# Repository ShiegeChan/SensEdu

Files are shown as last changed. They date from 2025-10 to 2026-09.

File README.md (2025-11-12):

<p align="center">
  
</p>

<p align="center"><b>Ultrasonic Ranging & Detection Development Shield for Arduino GIGA R1</b><br>
Designed for education - easy entry into ultrasonic sensing and research</p>

<p align="center">
  <a href="https://github.com/ShiegeChan/SensEdu/releases/" target="_blank">
    
  </a>
  <a href="https://github.com/ShiegeChan/SensEdu/commits/main" target="_blank">
    
  </a>
</p>

<b>
<p align="center">
	<a href="https://github.com/ShiegeChan/SensEdu/releases" target="_blank">Download</a> ·
	<a href="https://sensedu-shield.com/getting-started/" target="_blank">Getting Started</a> ·
	<a href="https://sensedu-shield.com/projects/" target="_blank">Example Projects</a> ·
	<a href="https://sensedu-shield.com" target="_blank">Documentation</a> ·
	<a href="https://sensedu-shield.com/contributing/" target="_blank">Contribution</a>
</p>
</b>

## Features

* **Custom Shield Design** for <a href="https://docs.arduino.cc/hardware/giga-r1-wifi/?queryID=undefined" target="_blank">Arduino GIGA R1 WiFi</a> and mechanically compatible boards (e.g., <a href="https://www.infineon.com/evaluation-board/KIT-A2G-TC375-ARD-SB" target="_blank">AURIX™ TC375 Shieldbuddy</a>). It extends the board with sensors:
  * **4x Infineon MEMS microphones**: capable of operating in ultrasonic range at approx. 20-80 kHz (<a href="https://www.infineon.com/assets/row/public/documents/24/49/infineon-im73a135-datasheet-en.pdf" target="_blank">datasheet</a>).
  * **2x Ultrasonic Transducers**: transmit ultrasonic waves with a center frequency of ~33kHz (<a href="https://www.farnell.com/datasheets/4413630.pdf?_gl=1*1fltz5c*_gcl_au*MTQwMTY3ODgxOC4xNzI2NDc2MDYw" target="_blank">datasheet</a>).
  * **2x Instrumentation Amplifiers**: providing 4x channels total, routed to external pin headers for connecting additional sensors such as surface EMG electrodes (<a href="https://www.analog.com/media/en/technical-documentation/data-sheets/ad8222.pdf" target= "_blank">datasheet</a>).
  * **1x Infineon Barometric Air Pressure Sensor**: provides pressure and temperature measurements; ideal for indoor and outdoor navigation, weather stations, drones, and more (<a href="https://www.infineon.com/dgdl/Infineon-DPS310-DataSheet-v01_02-EN.pdf?fileId=5546d462576f34750157750826c42242" target="_blank">datasheet</a>).
* **Low-Level SensEdu Library** for Arduino GIGA R1 that serves as a basic abstraction layer for the STM32H747 peripherals and provides default configurations for all sensors. It is implemented at the register level based on <a href="https://www.st.com/resource/en/reference_manual/rm0399-stm32h745755-and-stm32h747757-advanced-armbased-32bit-mcus-stmicroelectronics.pdf" target="_blank">STM32H747 Reference Manual</a> and <a href="https://developer.arm.com/documentation/ddi0403/latest/" target="_blank"> Armv7-M Architecture Reference Manual</a>, ensuring simplicity and expandability. Extensive examples are included to demonstrate library's functionality.
* **Example projects** show how to use SensEdu to achieve your learning goals. See the full implementation for pulsed time-of-flight distance measurements, FMCW ranging, FSK-modulated communication, a weather station, and other projects.
* **MATLAB scripts** enable visualization and post-processing of recorded data transferred via USB or Wi-Fi.

## Preview

<p align="center" style="margin:0">
  
  
  
  
  
</p>

## Installation

1. Download the latest release version from the <a href="https://github.com/ShiegeChan/SensEdu/releases" target="_blank">Download page</a>.
2. Extract the downloaded files and place the **libraries** folder into: `C:\Users\your_username\Documents\Arduino\`.
3. The **projects** folder can be placed anywhere in your system.
4. Open the <a href="https://www.arduino.cc/en/software" target="_blank">Arduino IDE</a> and install **Arduino Giga R1 board package** via the Boards Manager.

<p align="left" style="margin:0">
  
</p>
<p align="left" style="margin:0">
  
</p>

## Starting a Project

To get started, you can explore the hardware interface by following the examples provided in the SensEdu library (`Arduino\libraries\SensEdu\examples\`). A detailed description of all functions can be found in the <a href="https://sensedu-shield.com/library/" target="_blank">Documentation</a> under the "SensEdu Library" section.

In the `projects/` directory, you will find several complete projects designed for this board, including:
* **Ultrasonic Pulse-Echo Ranging**
* **Ultrasonic Pulse-Echo Ranging with Wi-Fi + GUI** - *in progress (25%)*
* **Ultrasonic Chirp Generation**
* **Ultrasonic FMCW Ranging**
* **Ultrasonic Doppler Velocimeter** - *coming soon*
* **Ultrasonic FSK Communication Link** - *coming soon*
* **EMG BioInputs** - *in progress (75%)*
* **Weather Station** - *in progress (50%)*

Detailed overview for each project is available in the "Projects" section of the <a href="https://sensedu-shield.com/projects/" target="_blank">Documentation</a>.

## Support

If you would like to contribute, please open a pull request!
Suggest improvements or check out already opened <a href="https://github.com/ShiegeChan/SensEdu/issues" target="_blank">issues</a> to help fix bugs or add new features.

## Acknowledgments

SensEdu was made possible thanks to these freely available tools:

* [Arduino] and [Arduino IDE 2.x]
* [XENSIV™ Digital Pressure Sensor Arduino Library]
* [STM32H747 Documentation] and [STM32CubeMX]
* [Jekyll] and [Just the Docs] template
* [KiCAD]

## License

* [**GPL-3.0 license**](https://github.com/ShiegeChan/SensEdu/blob/main/LICENSE)

[Arduino IDE 2.x]: https://github.com/arduino/arduino-ide
[Arduino]: https://www.arduino.cc/
[XENSIV™ Digital Pressure Sensor Arduino Library]: https://github.com/Infineon/arduino-xensiv-dps3xx
[STM32H747 Documentation]: https://www.st.com/en/microcontrollers-microprocessors/stm32h747-757/documentation.html
[STM32CubeMX]: https://www.st.com/en/development-tools/stm32cubemx.html
[Jekyll]: https://jekyllrb.com/
[Just the Docs]: https://github.com/just-the-docs/just-the-docs/tree/main
[STM32H747]: https://www.st.com/en/microcontrollers-microprocessors/stm32h747-757.html
[Arduino GIGA R1 WiFi]: https://docs.arduino.cc/hardware/giga-r1-wifi/
[KiCad]: https://www.kicad.org/

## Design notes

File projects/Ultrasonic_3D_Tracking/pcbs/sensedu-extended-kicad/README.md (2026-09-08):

# Extended SensEdu Shield (8 Microphones)

> [!WARNING]
> This PCB is a messy prototype that has never been cleaned up, and it may not work at all.
> It was created for the sole purpose of quickly testing an 8-microphone setup on a very old
> SensEdu revision, and is published for reference rather than for reproduction.

If you need an 8-microphone version, please contact us and we will help you with it.

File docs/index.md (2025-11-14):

---
title: Introduction
layout: home
nav_order: 1
description: "Ultrasonic ranging and detection development shield for Arduino GIGA R1, designed as an open-source educational project to lower the barrier to ultrasonic sensing and research."
permalink: /
---

# Introduction
{: .fs-8 .fw-500}

Welcome to the SensEdu documentation!
{: .fs-6 .fw-400}
---

SensEdu is an ultrasonic ranging and detection development shield for Arduino GIGA R1, designed as an open-source educational project to lower the barrier to ultrasonic sensing and research.
{: .fw-500}

Based on the [STM32H747] Microcontroller and runs on the [Arduino GIGA R1 WiFi] development Board, providing industry-standard embedded development experience while remaining beginner-friendly. SensEdu is perfect for students looking for a smooth introduction to this field, offering an easy-to-understand yet highly modifiable software and hardware environment. 

This project is completely open source and comes with quick support from the development team.

{: .WARNING}
SensEdu is still in its early development stages.
The core functionality is available, but many additional features are in progress. If you like the project, consider [contributing]({% link contributing/index.md %}). Any input from both experienced developers and beginners is highly appreciated!

## Features
{: .fw-500}

SensEdu includes:
{:.mb-1 .mt-3}
* MEMS microphones
* Ultrasonic Transducers
* Barometric Air Pressure Sensor

You can find detailed information about each component in the [PCB Chapter]({% link pcb/index.md %}). With these components, you can build a variety of projects, such as:
* Pulse-Echo and FMCW ultrasonic ranging
* Doppler Velocimeter
* FSK ultrasonic communication
* EMG signal controls
* Weather Station

## Project Structure
{: .fw-500}

The project is divided into three main parts:

* [Shield PCB]({% link pcb/index.md %}) – Located in `pcb\`
* [Hardware Abstraction Library]({% link library/index.md %}) – Located in `libraries\SensEdu\`
* [Full Projects]({% link projects/index.md %}) – Located in `projects\`

Each part is thoroughly documented in this wiki, allowing you to modify both software and hardware using the provided examples.

## Acknowledgments
{: .fw-500}

SensEdu was made possible thanks to these freely available tools:
{: .mb-1}
* [Arduino] and [Arduino IDE 2.x]
* [XENSIV™ Digital Pressure Sensor Arduino Library]
* [STM32H747 Documentation] and [STM32CubeMX]
* [Jekyll] and [Just the Docs] template
* [KiCAD]

Thank You to All Contributors!
{: .fw-500 .mb-1}

<ul class="list-style-none">
{% for contributor in site.github.contributors %}
  <li class="d-inline-block mr-1">
     <a href="{{ contributor.html_url }}">{{ contributor.login }}</a>
  </li>
{% endfor %}
</ul>

[Arduino IDE 2.x]: https://github.com/arduino/arduino-ide
[Arduino]: https://www.arduino.cc/
[XENSIV™ Digital Pressure Sensor Arduino Library]: https://github.com/Infineon/arduino-xensiv-dps3xx
[STM32H747 Documentation]: https://www.st.com/en/microcontrollers-microprocessors/stm32h747-757/documentation.html
[STM32CubeMX]: https://www.st.com/en/development-tools/stm32cubemx.html
[Jekyll]: https://jekyllrb.com/
[Just the Docs]: https://github.com/just-the-docs/just-the-docs/tree/main
[STM32H747]: https://www.st.com/en/microcontrollers-microprocessors/stm32h747-757.html
[Arduino GIGA R1 WiFi]: https://docs.arduino.cc/hardware/giga-r1-wifi/
[KiCad]: https://www.kicad.org/

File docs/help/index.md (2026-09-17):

---
title: Help
layout: default
nav_order: 6
permalink: /help/
---

# Getting Help
{: .fs-8 .fw-500 .no_toc}
---

Stuck? This page helps you solve the problem yourself or reach us if you can't.
{: .fw-500}

- TOC
{:toc}

## Before You Ask

Please start by trying to resolve the issue on your own:
* Read the [Getting Started]({% link getting started/index.md %}) section
* Use the search bar on this wiki (at the top of the page) to find related information by keywords
* Browse the [Frequently Asked Questions (FAQs)](#faqs) below
* Search online; your exact issue may already be answered

If you have tried the above and are still stuck, it is a good time to ask for help.

## Contact Us

The best way to reach us is on GitHub:
* [Issues] — confirmed bugs and planned work
* [Discussions] — everything else, including questions and ideas

If you want to keep things private, you can contact the SensEdu team directly via <a href="mailto:contact@sensedu-shield.com">contact@sensedu-shield.com</a>.

When asking for help:
* Avoid vague questions like "it doesn't work"
* Provide info on your OS, Arduino IDE version, SensEdu shield revision, and SensEdu library version
* Describe your hardware setup (wiring, sensors, power source)
* Tell us what you have already tried
* List the steps required to reproduce your issue
* Paste error messages as text and add screenshots if helpful

Your details will help us to answer your question!

Opening a new discussion on GitHub looks like this:

Discussions page of the SensEdu repository on GitHub

## FAQs

Here you can find the most frequently asked questions.

### How do I order the shield?
{: .no_toc}
Email us at <a href="mailto:contact@sensedu-shield.com">contact@sensedu-shield.com</a>.

### Why does my board not show up in the port list?
{: .no_toc}
Make sure you are using a USB cable that supports data transfer, and that the *Arduino Mbed OS Giga Boards* package is installed (see [Getting Started]({% link getting started/index.md %})). If the port is still missing, double-tap the reset button on the GIGA R1 to enter bootloader mode and select the port again. If it still fails, most likely your USB driver is installed incorrectly. Usually it ships together with Arduino IDE, so try to reinstall it. Ensure you have administrator rights during your installation.

### Why do I get `SensEdu.h: No such file or directory`?
{: .no_toc}
The library is not installed in the right place. Move the contents of the library folder from the [latest release][SensEdu release] to your Arduino libraries folder, as described in [Getting Started]({% link getting started/index.md %}):
* Windows: `C:\Users\{username}\Documents\Arduino\libraries\`
* Linux: `/home/{username}/Arduino/libraries/`
* macOS: `/Users/{username}/Documents/Arduino/libraries/`

Restart the Arduino IDE afterwards.

### How can I contribute?
{: .no_toc}
Start with the [Contributing Guide]({% link contributing/index.md %}) and create a [discussion][Discussions] on GitHub for your contribution, where we will discuss your ideas and help you get started!

[Discussions]: https://github.com/ShiegeChan/SensEdu/discussions
[Issues]: https://github.com/ShiegeChan/SensEdu/issues
[SensEdu release]: https://github.com/ShiegeChan/SensEdu/releases/

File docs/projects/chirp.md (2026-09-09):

---
title: Chirp Signal Generation
layout: default
math: mathjax
parent: Projects
nav_order: 3
---

# Chirp Signal Generation
{: .no_toc .fs-8 .fw-500}
---

## Table of contents
{: .no_toc .text-delta }
1. TOC
{:toc}

## Introduction
{: .text-yellow-300}

The **Chirp Signal Generation Project**{: .text-green-000} aims at providing basic code to generate **Frequency Modulated Continuous Wave (FMCW)** on the **SensEdu Shield**{: .text-green-000} using the **Arduino Giga R1**{: .text-green-000}. The projects provides two types of waveform for Linear Frequency Modulation (LFM): **sawtooth** and **triangular**.

A signal whose frequency varies over time is called **chirp**. Chirp signals are encountered in numerous fields, like radar and sonar systems, telecommunications, signal processing and more. Further information about potential applications are provided in the documentation of our FMCW ranging project. The following figures show an example of a chirp with frequency range between 100Hz and 10kHz, and the spectrogram of the same chirp, respectively.


{: .text-center}

_Chirp signal sweeping from 100Hz to 10kHz_
{: .text-center}


{: .text-center}

_Spectrogram of a chirp sweeping from 100Hz to 10kHz_
{: .text-center .}

## Chirp Generation Function
{: .text-yellow-300}
Arduino does not provide any built-in chirp signal function. There are workarounds using MATLAB's built-in chirp function but our idea was to create this signal directly in Arduino with the SensEdu library.

The `generate_sawtooth_chirp` and `generate_triangular_chirp` functions both calculate the values to generate a sawtooth chirp and triangular chirp respectively and copy these values to the DAC's buffer.

```c
void generate_sawtooth_chirp(uint16_t* array)
void generate_triangular_chirp(uint16_t* array)
```

### Parameters
{: .text-yellow-100}
* `uint16_t* array`: A pointer to an array where the generated chirp signal will be stored.

### Description
{: .text-yellow-100}
A full sine period is four mirrored copies of the same quarter wave, so only 0-90 degrees has to be stored. The chirp generating functions build the waveform from a lookup table:

* `lut_sine` is a LUT containing the values of a quarter sine wave. It holds `90 * LUT_RESOLUTION` entries, so `LUT_RESOLUTION` is the number of points stored per degree. A larger value results in a more detailed LUT, which in turn increases the precision of the chirp values which will be calculated.
* `chirp_value` holds the sample currently being computed, which is written straight into the DAC buffer.

The following steps describe how the function was implemented:

**Step 1**{: .text-blue-000}: Generate the quarter-wave LUT:

```c
// Generate the quarter-wave sine LUT
    for (int i = 0; i < 90 * LUT_RESOLUTION; i++) {
        phase_deg = (float)i * 90.0 / (90 * LUT_RESOLUTION); // Phase angle in degrees
        phase_rad = phase_deg * PI_F / 180.0; // Phase angle to radians
        lut_sine[i] = sin(phase_rad-PI_F/2); // Store sine value in the LUT
    }
```

**Step 2**{: .text-blue-000}: Calculate the instantaneous phase of the chirp signal and wrap between 0-360 degrees:

```c
for (int i = 0; i < samples_int; i++) {
        phase_rad = 2.0 * PI_F * (0.5 * chirp_rate * i / fs + START_FREQUENCY) * i / fs; // Phase angle in radians
        phase_deg = phase_rad * 180.0 / PI_F; // Phase angle to degrees
        phase_deg_wrapped = fmod(phase_deg, 360.0); // Wrap phase angle to 0-360 degrees
```

**Step 3**{: .text-blue-000}: Calculate the value of the chirp using a quadrant-based approach, then scale and offset to 12-bit and write it into the DAC buffer:

```c
        if (phase_deg_wrapped <= 90) {
            chirp_value = lut_sine[(int)(phase_deg_wrapped)* LUT_RESOLUTION+1] * 2048 + 2048;
        } else if (phase_deg_wrapped <= 180) {
            chirp_value = -lut_sine[(int)(180.0 - phase_deg_wrapped) * LUT_RESOLUTION+1] * 2048 + 2048;
        } else if (phase_deg_wrapped <= 270) {
            chirp_value = -lut_sine[(int)(phase_deg_wrapped - 180.0) * LUT_RESOLUTION+1] * 2048 + 2048;
        } else {
            chirp_value = lut_sine[(int)(360.0 - phase_deg_wrapped)* LUT_RESOLUTION+1] * 2048 + 2048;
        }

        array[i] = (uint16_t)chirp_value;
    }
```

For the triangular modulation, only the first half of the buffer is swept; the second half mirrors it to form the down-sweep.

```c
    // Mirror the up-sweep to form the down-sweep
    for (int i = half_samples; i < samples_int; i++) {
        array[i] = array[samples_int - i-1];
    }
```

{: .NOTE }
In this configuration, the first value of the chirp signal array is 0 (or 0 V in amplitude at DAC output). This initial value can be changed by modifying `lut_sine`.

---

## Main code
{: .text-yellow-300}
Check out the [DAC]({% link library/dac.md %}) section for more information on the DAC library and different DAC related functions.

The `Chirp_SawtoothMod.ino` and `Chirp_TriangularMod.ino` files contain the main code to generate the chirp signal, send the chirp signal to the DAC and enable the DAC.

The code contains the following user settings to adjust the chirp signal:

* `CHIRP_DURATION`{: .text-green-000}: The period of the chirp signal in seconds
* `START_FREQUENCY`{: .text-green-000}: The start frequency of the chirp signal in Hz
* `END_FREQUENCY`{: .text-green-000}: The end frequency of the chirp signal in Hz

A very important variable in the main code is the sampling frequency `fs`. Based on the Nyquist-Shannon sampling theorem, `fs` needs to be at least double the maximum frequency (or end frequency) of the chirp signal.
Keep in mind this sampling frequency will also be the DAC's output frequency in the `SensEdu_DAC_Settings` function.

{: .IMPORTANT }
`fs` needs to be at least 2*END_FREQUENCY in order for the chirp signal to be generated properly.

The `samples_int` is an integer representing the amount of samples for one period of the chirp signal. This value also represents the memory size in the `SENSEDU_DAC_BUFFER` and `SensEdu_DAC_Settings` functions.

The values of the chirp are printed in the serial monitor.
```c
// Print the chirp signal LUT
    Serial.println("start of the Chirp LUT");
    for (int i = 0 ; i < samples_int; i++) { // loop for the LUT size
        Serial.print("value ");
        Serial.print(i+1);
        Serial.print(" of the Chirp LUT: ");
        Serial.println(lut[i]);
    }
```

[example link]: https://github.com/ShiegeChan/SensEdu
[link1]: https://docs.github.com/en/get-started/writing-on-github/getting-started-with-writing-and-formatting-on-github/basic-writing-and-formatting-syntax
[link2]: https://just-the-docs.com/

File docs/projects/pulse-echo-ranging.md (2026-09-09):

---
title: Ultrasonic Ranging
layout: default
math: mathjax
parent: Projects
nav_order: 1
---

# Ultrasonic Ranging
{: .fs-8 .fw-500}
---

- TOC
{:toc}

## Introduction

Measuring distance is one of the most common measurements that have to be acquired in many applications across different fields. It referes to measuring distance, lenght or range of some object. The simplest way of measuring distance is using rulers. The more sophisticated methods are transit-time methods and interfereometer methods. 

Ranging is technique that measures distance or slant range from the observer to a target, especially a far and moving target. Active methods use unilateral transmission and passive reflection. Active rangefinding methods include laser (lidar), radar, sonar, and ultrasonic rangefinding. Ultrasonic ranging is mostly used in medical field, but it is becoming more popular in other fields and applications where, for example, solutions using radio waves are difficult to deploy due to its cost of production as well as the high computational demand. So in the cases where the focus is on cost reduction and design simplification, as well as when the limited operational range is not a concern, ultrasonic ranging can be a perfect solution. 

Using the SensEdu ultrasonic transducer, we demonstrate ranging technique using sound waves to obtain distance measurements between the transducer and an arbitrary object.  

The following sections will provide a step-by-step guide through the implementation of object ranging using ultrasound in three-dimensional space. 

## Theoretical concept 
An ultrasonic transciever transmits a short sound pulse with every high pulse power. The pulse is directed by the directivity of the speaker and propagates in the given direction with the speed of sound. 
If there is an obstacle (an object) in this direction, a part of the transmitted energy is scattered in all directions. A very small portion of the wave is also reflected back to the transciever. This information is received by the transducer and further evaluated to calculate the distance. Since the propagation of sound waves is constant, the distance is determined from the runtime of the high-frequency transmitted signal. The actual range of a target from the transducer is known as a slant range - a line of sight distance between the transciever and the object illuminated. The same working principle holds for radar systems which can be seen in the following animation. 

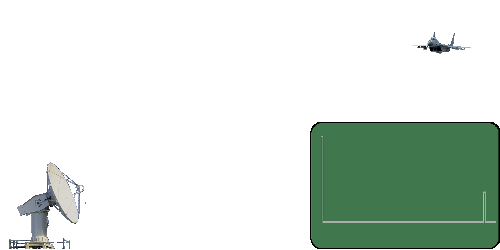
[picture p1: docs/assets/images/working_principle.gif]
 

The distance calculation is based on calculation of time difference between the sent pulse and the received pulse by the transciever. Therefore, the following is the formula for the slant range: 

$$
\begin{equation}
d = \frac{c\cdot t}{2}
\label{eq:slant range}
\end{equation}
$$

where *t* is the measured runtime in seconds, *c* is the speed of sound in air (343 m/s) and d is the slant range in meters. 

## Hardware Setup 

The following section describes the hardware used to obtain the distance measurements. First, the system architecture is shown. 

We use SensEdu transducer board equipped with two ultrasonic speakers and four MEMS microphones with resonant frequencies in ultrasonic range. The microphones are placed in a square shape configuration. The board is connected to Arduino GIGA R1 equipped with STM32 microcontroller.

 

## Signal Processing

When the audio signal is acquired and it goes through ADC module, a digital representation of the sound wave is the start of the signal processing chain. We call this signal the raw signal. To get the information about the distance, we use the cross-correlation technique. It compares the received signal with the sent signal and the time where the similarity between the two signals is the highest, corresponds to the distance of the detected object. 

The following data acquisition flow chart explains the algorithm. 
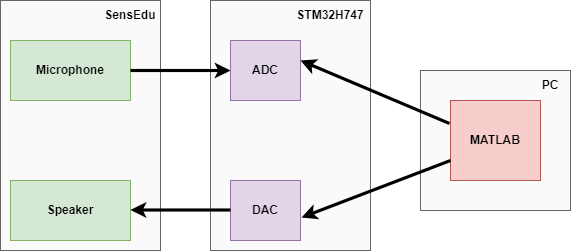
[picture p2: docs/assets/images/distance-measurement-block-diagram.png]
 

To generate the measurements, first burst sine signal with 32kHz frequency is sent through DAC to the speaker. The sine wave is stored in a lookup table (LUT). 

After the burst is sent, ADC starts to collect the data microphones are receiving. The raw data is represented with 16bit values corresponding to the changes in pressure received by microphones. 

### Rescaling the ADC signal
The ADC signal has values in range [0, 65535]. Therefore, we first rescale the signal to the range [-1, 1] with each sample being a 4-byte float value. 

```c
void rescale_adc_wave(float* rescaled_adc_wave, uint16_t* adc_wave, size_t adc_data_length) {
    // 0:65535 -> -1:1
    for(uint16_t i = 0; i < adc_data_length; i++) {
        rescaled_adc_wave[i] = (2.0f * adc_wave[i])/65535.0f - 1.0f;
    }
}
```

{: .NOTE}
Because of the way multi-channel ADC signals are stored in memory using SensEdu library, the channel number has to be passed to the function we are using. 

### Filtering the rescaled signal

The microphones have a large bandwidth of 100kHz and the signal is easily distorted by the audible sound. That is why the filtering around the central frequency of 32kHz is needed. Therefore, a Finite Impulse Response (FIR) bandpass filter is applied to the previously resacaled ADC signal. The filter also removes the unwanted DC component, as well as high-frequency noise that is also naturally present. 

```c
void filter_32kHz_wave(float* rescaled_adc_wave, uint16_t adc_data_length) {
    static float32_t output_signal[STORE_BUF_SIZE];
    // initialize this temporal buffer
    clear_float_buf(output_signal, STORE_BUF_SIZE);
    // need to take block chunks of the input signal
    for(uint16_t i = 0; i < adc_data_length; i += FILTER_BLOCK_LENGTH) {
        // take care of the last block
        size_t block_size = min(FILTER_BLOCK_LENGTH, adc_data_length - i);
        // perform the filter operation for the current block
        arm_fir_f32(&fir_filt, &rescaled_adc_wave[i], &output_signal[i], block_size);
    }
    memcpy(rescaled_adc_wave, output_signal, adc_data_length * sizeof(float));
}
```

### Cross-correlation
Finally, the cross-correlation method is performed on the filtered signal and output signal from the speaker. The result of the cross-correlation is number of lag samples between the two signals. Then, the distance is computed as: 

$$
\begin{equation}
d = \frac{(lag\_samples \cdot sample\_time)}{sampling\_rate \cdot 2}
\end{equation}
$$ 

There are two modes available for sending the data to the PC by setting a value of a macro. Setting `IS_TRANSMIT_DETAILED_DATA` to *true* sends the complete raw-, rescaled-, and filtered data with distance measurements to the PC. Otherwise, only the distance measurements will be sent to the PC.  

{: .NOTE}
For faster measurements, cross-correlation is performed directly on the microcontroller. Sending the intermediate
processing steps to the PC costs a lot of transfer time, so keep `IS_TRANSMIT_DETAILED_DATA` off unless you need them.

```c
void custom_xcorr(float* xcorr_buf, const uint16_t* dac_wave, uint32_t adc_data_length) {
    // delay loop
    for (int32_t m = 0; m < adc_data_length; m++) {
        // sum loop
        float sum = 0;
        for (uint16_t n = 0; n < dac_wave_size; n++) {
            uint32_t idx = n + m;
            if (idx < adc_data_length) {
                sum += dac_wave[n]*xcorr_buf[idx]; 
            }
        }
        xcorr_buf[m] = sum; 
    }
}
```

## Receiving the Data

The communication is done using a Half Duplex method and UART communication protocol - each sender and receiver can transmit the data but not at the same time. This is needed since the data acqusition is started only after the PC (sender) sends the starting signal to the board. After the starting signal, data acquisition and data sending is performed for a predefined amount of time. 

Since we are using serial communication, the data is received one bit at a time. To start receiving the data from the microcontroller, the PC initiates the communication by sending the starting byte. 

Serial communication between the mcu and the pc
{: .text-center}

This diagram depicts one iteration of PC receiving the data. This continues for number of iterations that are specified in the MATLAB script. Then, the data is plotted for visualization.

{: .IMPORTANT}
Make sure that `ENABLE_DETAILED_DATA` in MATLAB matches the value of `IS_TRANSMIT_DETAILED_DATA` in the firmware, that `MAX_PEAKS` in MATLAB matches `Peaks.h`, and that `DATA_LENGTH` in MATLAB matches the `STORE_BUF_SIZE` macro. Make sure to choose the correct `ARDUINO_PORT` to match the real one. 

## Showcase 

This section shows an examople of determining the object distance using the described protocol above. When there is no object in the defined field of view (FOV) of the measurement system, the raw signal of the microphone looks the following way:

 

The peak showing in the first samples of the signal represents the audio-coupling effect coming from the speaker that transmits the inital pulse. This determines the minimum anambiguous distance that can be measured by the object and it corresponds to about 20cm from the measurement system. 

If there is an object in the defined FOV, the signal shows two peaks, the second representing the object distance:

 

By moving the object in space, the peak will move in time accordingly. Using the above formula, considering the speed of sound in the air constant, the distance value can be determined. 

The following figure represents the measurement acquisition in time, portraying the intermediate processing steps as well. The first column represents the distance in time, while the last three columns represent the current measurement being taken. Each row represents measurements for each microphone on the board. 

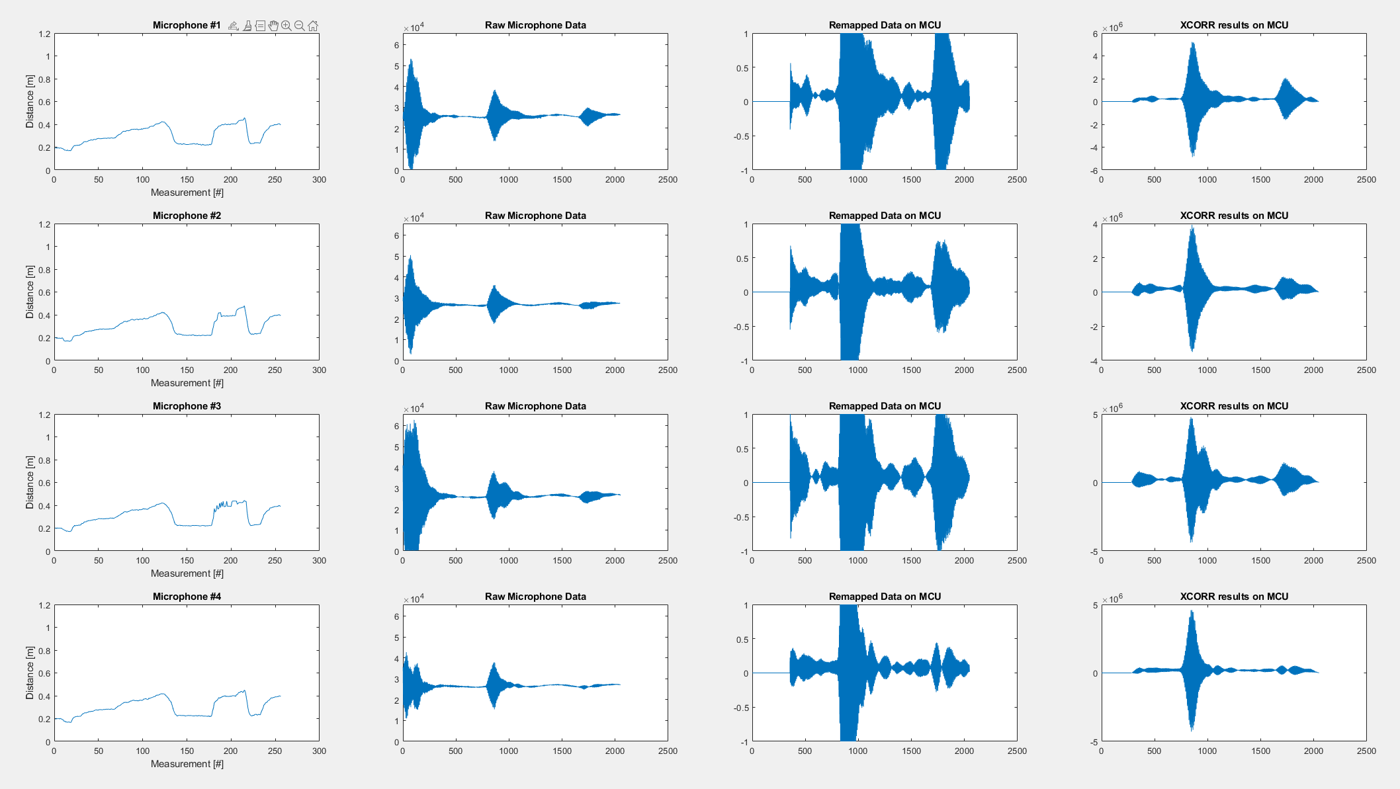
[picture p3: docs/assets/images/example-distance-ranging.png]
 

## Considerations and improvements
The quality of the measurements received is highly dependent on many different aspects, one of the most influential being the characteristic of the object itself. The precision of the object distance depends on its size and material, as well as speed of the object in case it is moving. For example, larger object and object made of material with high reflectivity will result in better measurements than the small object with lower reflectivity. This fact also determines the maximum phyiscal range at which an object can be measured, and it is not absolute. The reflectivity of the object is very important since it directly influences the strength of the reflected signal. When the signal reflection is weak, the measurement more difficult to obtain. 

Another thing to consider is that the algorithm is suitable for distance measurement of a single object. In case there are multiple object in FOV, there is no way to distinguish between them. A good improvement could be resolving this issue and simultaniously recieve the distance of multiple objects. 

## Reference
[Radar Working Principle](https://www.radartutorial.eu/01.basics/Distance-determination.en.html)

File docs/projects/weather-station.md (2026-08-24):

---
title: Weather Station
layout: default
math: mathjax
parent: Projects
nav_order: 8
---

# Weather Station
{: .no_toc .fs-8 .fw-500}
---

- TOC
{:toc}

## Introduction

Weather Station is a project intended to demonstrate the usage of barometric air pressure [DPS368] and humidity [SHT40-AD1F] sensors on the SensEdu shield. 

This turns the board into a small environmental measurement station that reports temperature, humidity, dew point, and sea-level pressure every few seconds, along with classifications of each quantity. The station also tracks how the sea-level pressure changes over time and reports a simple forecast of the improving or worsening of the conditions.



## Background

This section presents what some of the measured quantities mean and why they are useful for determining the environmental conditions.

### Humidity

Humidity is the amount of water vapor in the air. It could be represented in three different ways.

#### Absolute Humidity (AH)
{: .no_toc}

The mass of water vapor **per volume of air**.

#### Specific Humidity (SH)
{: .no_toc}

Intuitively, AH feels like the right metric to describe the absolute water vapor in the air, but it is actually true **only if the volume is constant as well** (imagine sealed rigid container).

But in the case of open air which is more typical for meteorological measurements, volume is not constant. For example, heating up the air at typical atmospheric pressure makes it expand, which leads to the same mass of vapor spreading through a larger air volume, so absolute humidity actually *decreases*.

Therefore, there exists another vapor metric which is independent of volume changes called **specific humidity** (SH), defined as the mass of water vapor per unit **mass of moist air**.

#### Relative Humidity (RH)
{: .no_toc}

Defined as the ratio of the current water-vapor content to the maximum the air could hold at the same temperature, expressed as a percentage.

RH depends on **both** water vapor content and temperature: warmer air can hold more water, meaning heating the air with certain specific humidity will actually *lower* its RH even though no water has been removed. Conversely, cooling the air will *raise* its RH.

This brings us to the main caveat of RH — it is not a great way to determine how the humidity feels to a person. Much of our perception of humidity comes from how easily sweat can evaporate from the skin. For this reason, the **dew point** is a more intuitive measure of perceived humidity than RH.

### Dew Point

Dew point is the temperature to which the air would have to be cooled (at constant [specific humidity](#specific-humidity)) for it to start condensing into dew or fog. Unlike RH, the dew point is an absolute property of the air's water content, expressed in °C. Two different air samples with the same dew point hold the same amount of water vapor regardless of their current temperatures or RH. It helps avoid misleading humidity decisions just based on the RH, which can change with temperature even if the specific humidity is constant.

This metric makes for a useful comfort indicator, tracking the actual moisture content of the air, which is what makes it feel sticky or dry. You can read more about the relation to human comfort [here](https://en.wikipedia.org/wiki/Dew_point#Relationship_to_human_comfort).

To calculate the dew point from the sensor readings, the [Magnus formula](https://en.wikipedia.org/wiki/Dew_point#Calculating_the_dew_point) is usually used, expressed as:

$$\gamma(T, RH) = \ln\!\left(\frac{RH}{100}\right) + \frac{aT}{b + T}$$

$$T_d = \frac{b \cdot \gamma(T, RH)}{a - \gamma(T, RH)}$$

* $$T_d$$ -- dew point (°C)
* $$T$$ -- temperature (°C)
* $$RH$$ -- relative humidity (%)
* $$a = 17.625$$, $$b = 243.04$$ °C -- empirical fitting constants, optimized for the range −40 °C to +50 °C

### Dew Point Depression

Dew point depression $$(T − T_d)$$ is the difference between the temperature and dew point temperature. A small dew point depression indicates that the air is close to saturation, which can lead to the formation of fog or mist. Respectively, a large dew point depression indicates that the air is relatively dry and less likely to produce condensation.

### Atmospheric Pressure

Atmospheric pressure is the force per unit area that the atmosphere exerts on the Earth's surface, caused by the weight of the air above. You can find a more detailed explanation [here](https://www.noaa.gov/jetstream/atmosphere/air-pressure). The important thing is that pressure gradients are a main driver of weather patterns. Air drifts across regions, and changes in pressure are directly associated with different weather conditions.

As a rule of thumb, high pressure is associated with clear skies and calm conditions, while low pressure is associated with clouds and [precipitation](https://en.wikipedia.org/wiki/Precipitation). Since high and low pressure are relative concepts, a reference value was defined, called the **standard sea-level pressure of 1013.25 hPa** measured at 0 altitude.

Since the pressure decreases with altitude, a raw reading from a station at, say, 500 m above sea level cannot be compared directly against the sea-level reference. For that reason, the standard way is to recalculate the pressure to its **sea-level equivalent** using the location altitude and the current temperature. This way, the reading can be compared against the reference and classified properly.

Calculation is done using the [barometric formula](https://en.wikipedia.org/wiki/Barometric_formula#Model_equations):

$$P_0 = P \cdot \left[\frac{T}{T_0}\right]^{\dfrac{g'_0 M_0}{R^* L}}$$

* $$P_0$$ -- sea-level equivalent pressure (Pa)
* $$P$$ -- pressure at weather station (Pa)
* $$T$$ -- temperature at station (K)
* $$T_0$$ -- temperature at sea level (K)
* $$L$$ -- temperature [lapse rate](https://en.wikipedia.org/wiki/Lapse_rate#Mathematics_of_the_adiabatic_lapse_rate) (K/m); $$-6.5$$ K/km at sea level
* $$h$$ -- station altitude (m)

Temperature at sea level ($$T_0$$) can be calculated by extrapolating from the station temperature ($$T$$) using the lapse rate:

$$T_0 = T - L \cdot h = T + 0.0065 \cdot h$$

The exponent is a constant:

$$\dfrac{g'_0 M_0}{R^* L} = \dfrac{9.8\,\text{m/s}^2 \cdot 0.03\,\text{kg/mol}}{8.31\,\text{J/(mol·K)} \cdot (-6.5\,\text{K/km})} \approx -5.257$$

* $$g'_0$$ -- standard gravity (9.80665 m/s²)
* $$M_0$$ -- mean molar mass of air at sea level (28.9644 kg/kmol)
* $$R^*$$ -- universal gas constant (8.31432 J/(mol·K))

Thus, the formula simplifies to:

$$P_0 = P \cdot \left[\frac{T}{T + 0.0065 \cdot h}\right]^{-5.257} = P \cdot \left[1 + \frac{0.0065 \cdot h}{T}\right]^{5.257}$$

{: .NOTE}
Do not forget to convert degrees Celsius to Kelvin by adding $$273.15$$ to the station reading.

After proper conversion the pressure can be classified as high or low. But rather than flat labels, the much more useful information is the **pressure trend** over the last few hours. This is what actually predicts in which direction the weather is developing. A rising trend is associated with improving conditions, while a falling trend is associated with worsening conditions and higher chances of precipitation.

There is a classic forecasting nomogram called [Zambretti Forecaster] which predicts weather based on current pressure and the pressure trend. It claims to be 94% accurate when calibrated in its home UK climate.

## Hardware Setup

Connect the shield to Arduino GIGA R1 as usual, and access both [DPS368] and [SHT40-AD1F] sensors via the primary I2C bus at pins 20 (SDA) and 21 (SCL).

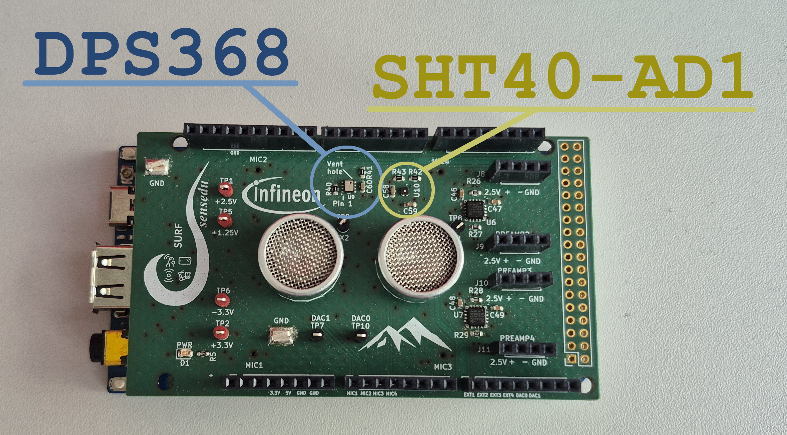
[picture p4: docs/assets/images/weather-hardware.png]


To use the primary I2C bus you need to include the `Wire` library in Arduino sketch and call the `Wire.begin()` in the setup function.

{: .NOTE}
Ensure to use `Wire` specifically, not the `Wire1` or `Wire2`. They refer to different I2C buses. Refer to [Arduino GIGA R1 I2C section](https://docs.arduino.cc/tutorials/giga-r1-wifi/cheat-sheet/#i2c-pins) in the documentation for more details.

For I2C communication each sensor has assigned address. The DPS368 uses `0x77` and the SHT40-AD1 `0x44`. You can verify it and the basic communication in general via an I2C scanner sketch (see [Developer Notes](#i2c-scanner)), which is provided in the `projects/Weather_Station/scanner/` directory. The expected output should show both addresses as active on `Wire` bus.



Communication is actually established by the third-party sensor libraries, which are included as dependencies in the sketch. The libraries handle all low-level I2C transactions, so the weather station just calls their high-level APIs to get the measurements.

* Infineon DPS368: [`arduino-xensiv-dps3xx`](https://github.com/Infineon/arduino-xensiv-dps3xx).
* Sensirion SHT40-AD1: [`arduino-i2c-sht4x`](https://github.com/Sensirion/arduino-i2c-sht4x) 

SHT40-AD1 library example has a problem with its compilation on Arduino GIGA R1. The patched one is available in the `projects/Weather_Station/sht4x_example/` directory, and the issue is described in more detail in the [Developer Notes](#sht4x-example-compilation-error) section below.

## Code Layout

The sketch is split into multiple `.ino` files. Arduino concatenates them all together at compile time, so they share global state without explicit `#include`s between them. The shared types live in a real `.h` header for proper include order.

| File | Purpose |
|---|---|
| `Weather_Station.ino` | Entry point. Holds all user-tunable `#define` macros, the global sensor objects, `setup()`, and `loop()`. The loop performs one read + compute + display cycle. |
| `sensors.ino` | Three `measure_*()` wrappers that call the libraries and return `false` on error. Pure I/O. |
| `metrics.ino` | All math (sea-level pressure, dew point) and all printing (each `report_*()` formats one row of the serial dashboard, with a `classify_*()` helper for the readable status label). |
| `pressure_trend.ino` | Implements pressure trend. A circular buffer captures one sea-level pressure sample every `PRESSURE_PERIOD_MIN` minutes; `try_get_pressure_trend()` runs a least-squares regression over the recent window. |
| `pressure_types.h` | The two structs (`PressureSample`, `PressureTrendStatus`) shared between the trend sketch and the report printer. |

## Configuration

All knobs live as `#define` macros at the top of `Weather_Station.ino`:

| Macro | Default | Meaning |
|---|---|---|
| `DEBUG_WAIT_FOR_SERIAL` | 0 | Set to 1 to make `setup()` block until a serial monitor connects. Useful when debugging `setup()`. |
| `ALTITUDE_M` | 501.0 | Station altitude above mean sea level, in meters. |
| `DISPLAY_PERIOD_SEC` | 5 | Seconds between display refreshes. Sensor reads happen at this same rate. |
| `PRESSURE_PERIOD_MIN` | 30 | Minutes between captures into the pressure-trend buffer. The trend window length is `PRESSURE_PERIOD_MIN * PRESSURE_TREND_SAMPLES`. |
| `PRESSURE_HISTORY_SIZE` | 48 | Total slots in the circular history buffer (24h with the defaults). |
| `PRESSURE_TREND_SAMPLES` | 6 | Number of recent samples the regression uses. Together with `PRESSURE_PERIOD_MIN` defines the trend window (3h with the defaults). |
| `SHT_AS_TEMP_SOURCE` | 1 | Which sensor's temperature reading is used as "ambient" for display. Dew point itself always uses the SHT (see [Developer Notes](#dew-point-calculation)). |
| `DPS_OVERSAMPLING_RATE` | 5 | DPS368 oversampling exponent (0–7). The sensor takes $$2^N$$ internal samples per result; more accurate but slower. |
| `DPS_TEMP_OFFSET` | −3.0 °C | Empirical offset subtracted from the DPS temperature to compensate for self-heating on this PCB. |
| `SHT_TEMP_OFFSET` | −2.5 °C | Same, for the SHT4x. |

{: .NOTE}
Ideally, the offsets should be determined experimentally with a known-good reference thermometer in the same environment as the station.

## Firmware Implementation

This section will describe the general idea behind the firmware implementation. Refer to the full source code under `/projects/Weather_Station/` for the complete picture.

### Sensor Initialization

There is one global object for each sensor. The `setup()` function then calls their `begin()` methods directly as described in examples by the respective libraries.

```c
#include <Dps3xx.h>
#include <SensirionI2cSht4x.h>

SensirionI2cSht4x sht_sensor;
Dps3xx dps_sensor = Dps3xx();

void setup() {
    Wire.begin();
    Serial.begin(9600);
    dps_sensor.begin(Wire);
    sht_sensor.begin(Wire, SHT40_I2C_ADDR_44);
    sht_sensor.softReset();
    delay(10);
}
```

### Measurements
The `measure_*()` functions in `sensors.ino` are simple wrappers around the library calls that return `false` on any error, so the main loop can decide how to handle it. Example for DPS368 temperature measurement:

```c
bool measure_dps_temp(float* temp) {
    int16_t err = dps_sensor.measureTempOnce(*temp, DPS_OVERSAMPLING_RATE);
    if (err != 0) {
        Serial.print("Failed DPS Measurement. DPS lib error code: ");
        Serial.println(err);
        return false;
    }
    return true;
}
```

### Main Loop

1. **Raw data acquisition from both sensors**: No offsets are applied yet. If any sensor errors out, the cycle is aborted.
2. **Dew point calculation**: [Magnus formula](#dew-point) applied to the raw SHT temperature/humidity pair. The SHT is always used here, since the dew point requires T and RH from the same physical state of the air — using a matched pair from the same sensor improves accuracy (see [Developer Notes](#dew-point-calculation)).
3. **Ambient temperature**: The empirical offset configured by the user is applied to get a corrected ambient temperature, rather than taking the temperature exactly at the sensor point on the PCB.
4. **Ambient relative humidity**: Recomputed from the corrected ambient temperature and the (already-locked-in) dew point, using the Magnus formula in reverse (see [Developer Notes](#ambient-rh)). This is the RH a person standing next to the device would experience, not the RH at the sensor surface.
5. **Dew point depression**: The dew point is subtracted from the ambient temperature.
6. **Sea-pressure conversion**: Recomputation of the pressure reading to equivalent [sea-level pressure](#sea-level-pressure) using the ambient temperature and specified altitude.
7. **Fill the pressure trend buffer**: At configured intervals the sea-level pressure is saved into the circular buffer.
8. **Pressure trend calculation**: If enough samples have been collected, the trend is computed via [least-squares regression](https://en.wikipedia.org/wiki/Least_squares).
9. **Print the dashboard**: All values are displayed in three columns: metric label, value, and classifier tag.

The full output of one cycle looks like this:

```
====== Weather Report ======
Temperature     22.43 °C
Humidity        48.54 %         Comfortable
Dew Point       11.05 °C        Comfortable
Dew Depression  11.38 °C        Fog Unlikely
Altitude        501.00 m
Pressure (raw)  954.32 hPa
Pressure (sea)  1015.78 hPa     Normal
Pressure Trend  -0.42 hPa/h     Worsening (next in 0:14)
============================
```

## Classification

Each measured quantity is mapped to a short human-readable label by a small `classify_*` helper in `metrics.ino`. I attempted to find the standard for each of the metrics and assign them accordingly.

### Relative Humidity
{: .no_toc}

As discussed above, labeling RH is not straightforward — it is heavily affected by temperature, so the same value can feel very different on a cold morning versus a hot afternoon. It is most meaningful indoors, where room temperature stays relatively stable. For that reason, formal guidance only defines the comfortable range; the surrounding bands are informal extensions. 

The "Comfortable" band is taken from the [US EPA indoor air quality guidance](https://www.epa.gov/mold/mold-course-chapter-2#Chapter2Lesson3), which recommends keeping indoor RH below 60%, ideally between 30% and 50%.

| Relative Humidity (%) | Project Label |
|---|---|
| < 30 | Dry |
| 30–60 | Comfortable |
| 60–75 | Humid |
| 75–90 | Very Humid |
| ≥ 90 | Saturated |

### Dew Point
{: .no_toc}

Dew point maps fairly directly onto perceived comfort — better than relative humidity, since it's an absolute measure of moisture in the air.

The structural source is the [Australian Bureau of Meteorology](https://media.bom.gov.au/social/blog/1324/feeling-hot-and-bothered-its-not-the-humidity-its-the-dew-point/). It offers a six-band scale calibrated for Brisbane's humid subtropical climate. BOM's thresholds somewhat line up well with what the [Deutscher Wetterdienst](https://www.dwd.de/DE/wetter/thema_des_tages/2020/6/21.html) describes for Central Europe. Specifically, a "Schwülegrenze" (sultriness threshold) is defined around 16–17 °C, and ≥ 20 °C is said to be "ziemlich unangenehm" (quite unpleasant). 

Two adjustments have been made — dew points above ~22 °C are essentially never seen in Central Europe, so BOM's upper "Oppressive" band is pulled down. At the same time, the lower bands are relabelled upward. What BOM calls "dry" is normal in Central Europe's drier baseline climate, so the project treats lower range as "comfortable."

| Dew Point (°C) | Project Label | BOM (Brisbane) |
|---|---|---|
| < 5  | Dry | Very dry |
| 5–15 | Comfortable | Dry (BOM: 5-10); Comfortable (BOM: 10-15) |
| 15–20 | Muggy | Starting to feel muggy (BOM: 15–20) |
| 20–22 | Oppressive | Muggy and quite uncomfortable (BOM: 20–24) |
| > 22 | Miserable | Oppressive (BOM: > 24) |

{: .NOTE}
Climate acclimatisation matters. People adapted to more humid climates tolerate higher dew points; Central Europeans are accustomed to a drier baseline than Australians and may find discomfort sets in earlier than the BOM scale suggests.

### Dew-point Depression
{: .no_toc}

Dew-point depression (also called spread) can be used to estimate the likelihood of fog formation. The smaller the spread, the closer the air is to saturation and the higher the chances of condensation occurring. The 2.5 °C threshold is given by the [NWS fog guide](https://www.weather.gov/media/zhu/ZHU_Training_Page/fog_stuff/fog_guide/fog.pdf).

| Spread (°C) | Label |
|---|---|
| < 2.5 | Fog Likely |
| ≥ 2.5 | Fog Unlikely |

### Sea-level Pressure
{: .no_toc}

The standard sea-level pressure of 1013.25 hPa is defined by the [International Standard Atmosphere](https://en.wikipedia.org/wiki/International_Standard_Atmosphere). The "Normal" band contains the reference value. For the surrounding bands I used 10 hPa steps based on my measurements and comparison with weather at my location and also partially derived from labels used in [Zambretti Forecaster].

| Pressure (hPa) | Label |
|---|---|
| ≥ 1030 | Very High |
| 1020–1030 | High |
| 1010–1020 | Normal |
| 1000–1010 | Low |
| 990–1000 | Very Low |
| 980–990 | Extremely Low |
| < 980 | Storm |

### Pressure Trend
{: .no_toc}

Pressure tendency is a key predictor of weather changes. A rising pressure usually indicates improving weather, while a falling pressure suggests worsening conditions and higher chances of precipitation. The named categories come from the UK Met Office shipping forecast terminology, [as documented by All At Sea](https://www.allatsea.net/weather-forecasting-barometer/), which gives fixed three-hourly amounts for four of the six categories:

* slowly (0.1–1.5 mb)
* rising/falling (1.6–3.5 mb)
* quickly (3.6–6.0 mb)
* very rapidly (> 6.0 mb)

This project measures pressure changes in hPa/h, so the above amounts are divided by 3 to get the per-hour equivalents. A "Steady" band is added around zero to avoid over-sensitivity to small fluctuations. "Improving" and "Worsening" span the normal rising/falling range; "Clearing" and "Storm Incoming" cover both the quickly and very rapidly changing conditions, in the rising and falling directions respectively.

| Trend (hPa/h) | Label |
|---|---|
| > +1.2 | Clearing |
| +0.5 … +1.2 | Improving |
| −0.5 … +0.5 | Steady |
| −1.2 … −0.5 | Worsening |
| < −1.2 | Storm Incoming |

## Showcase

{: .WARNING}
Do not measure under direct sunlight or near a heat source, as it will bias the temperature readings and thus all the derived metrics. The station is designed to be used in the shade or indoors.

{: .TIP}
If you find your readings being off from official weather reports, sometimes it can be expected in your specific measuring conditions. For example, the temperatures are generally higher close to the buildings. Most comparable conditions are usually in open air, e.g. on the roof or open field.

The station was tested at Villach, Austria (501m) at 19:00 CEST on 13.05.2026, during a clear sky day with a light breeze and coming heavy rain later.

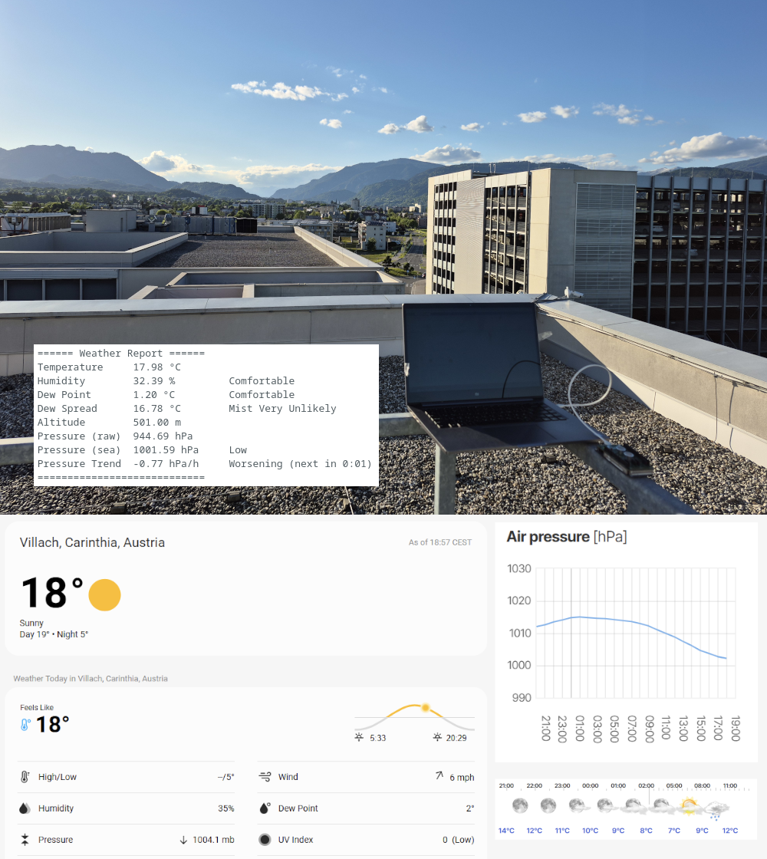
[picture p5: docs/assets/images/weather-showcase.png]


## Developer Notes

### SHT4x Example Compilation Error

The example `arduino-i2c-sht4x/examples/exampleUsage/exampleUsage.ino` shipped with the Sensirion SHT4x library does **not** compile out of the box on the Arduino GIGA R1.

The compiler says:

```
error: 'int16_t error' redeclared as different kind of symbol
 static int16_t error;
                ^~~~~
note: previous declaration 'void error(const char*, ...)'
 MBED_NORETURN void error(const char *format, ...) MBED_PRINTF(1, 2);
                    ^~~~~
```

The problem is that the example declares a file-scope variable named `error` which already exists in Mbed Arduino Core at `mbed_error.h`. Both symbols live in the global namespace, so the compiler refuses to compile the sketch. The example is fixed in the patched copy under `projects/Weather_Station/sht4x_example/` by renaming SHT error variable to `sht_error`.

{: .TIP}
Relevant [Pull Request](https://github.com/Sensirion/arduino-i2c-sht4x/pull/19).

### I2C Scanner

The typical Arduino I2C scanner found online cannot detect the SHT4x on Arduino GIGA. The classic pattern relies on a zero-byte write to probe each address, which works for most sensors including DPS368, but SHT4x is a command-driven sensor that will not ACK unless a valid command byte is received. The reliable workaround is to send a 1-byte write of a dummy value and accept as "device present" both `I2C_OK` (device ACKed everything) and `I2C_ERR_DATA_NACK` (address ACKed but data byte NACKed).

A scanner that uses this probe and walks both `Wire` and `Wire1` is provided under `projects/Weather_Station/scanner/`.

### Dew Point Calculation

Two subtle pitfalls when computing dew point from sensor data:

{: .WARNING}
Do not apply the empirical temperature offset before calling the Magnus formula.

The `DPS_TEMP_OFFSET` / `SHT_TEMP_OFFSET` constants in `Weather_Station.ino` exist to compensate for sensor self-heating. When a sensor self-heats, its temperature reading rises and its humidity reading falls as well. The two shift together so that the dew point derived from the pair remains correct. 

The (T, RH) pair is self-consistent and feeds Magnus a physically valid state. If you apply the offset before dew point computation, you lower the temperature while leaving the humidity unchanged, breaking that pairing and biasing the computed dew point a few degrees too low.

{: .WARNING}
Always use the SHT temperature, not the DPS temperature.

The Magnus formula assumes T and RH describe the same physical state of the air. The SHT4x measures both quantities from the same silicon die at the same instant — a guaranteed-consistent pair. Mixing the DPS368's temperature reading with the SHT4x's humidity reading combines two sensors with different self-heating profiles, mounted on different parts of the PCB, sampled at slightly different times.

The `SHT_AS_TEMP_SOURCE` macro in `Weather_Station.ino` controls only which sensor provides the *displayed* ambient temperature (and feeds the sea-level pressure conversion).

### Ambient RH

Ambient temperature is acquired by subtracting the empirical offset from the raw sensor reading. Relative humidity cannot be corrected the same way — it depends on temperature, so simply subtracting an offset from the raw RH value would give a wrong result. The correct approach is:

1. Read raw SHT temperature and humidity
2. Compute dew point from the raw `(T, RH)` pair. This locks in the air's specific humidity.
3. Apply the temperature offset to obtain the corrected ambient temperature.
4. Recompute relative humidity from the corrected temperature and the dew point (invert the Magnus formula). This gives the RH the air actually has at the ambient temperature, not the RH the hot sensor surface saw.

The main principle behind is that **dew point is a property of the air's specific humidity**. It does not depend on the sensor's temperature, the displayed temperature, or any offset. Once it has been derived from a self-consistent raw measurement, it becomes the anchor for everything moisture-related.

[Zambretti Forecaster]: https://web.archive.org/web/20110610213848/http://www.meteormetrics.com/zambretti.htm
[DPS368]: https://www.infineon.com/part/DPS368
[SHT40-AD1F]: https://sensirion.com/de/produkte/katalog/SHT40-AD1F

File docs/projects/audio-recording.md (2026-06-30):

---
title: Audio Recording
layout: default
math: mathjax
parent: Projects
nav_order: 6
---

# Audio Recording
{: .no_toc .fs-8 .fw-500}
---

- TOC
{:toc}

## Introduction

The Audio Recording project turns SensEdu into a continuous PCM audio recorder. Microphone data is sampled at 44.1 kHz, buffered locally on the board, and streamed over USB to a MATLAB host that saves it as a WAV file and plots its time-domain waveform and spectrum.

The project is built around a problem: **the USB transfer that is supposed to deliver the recording also injects noise into the analog input**. The architecture is designed to limit USB transfers to brief bursts, so the noise appears only at the segment boundaries instead of being spread across the whole recording. This project covers DMA double-buffering, external SDRAM, framed serial protocols, and recoverable error handling – all common building blocks of more advanced acquisition systems.

## Background

### PCM Audio

Pulse Code Modulation (PCM) represents an analog audio signal digitally using two main parameters:

* **Sampling rate** ($$F_s$$): how often the ADC samples the input. CD audio uses $$F_s = 44.1\text{ kHz}$$, which covers the full audible range.
* **Bit depth**: the resolution of each sample. The STM32H7 ADC in this project produces 16-bit values.

A 30-second recording at these settings is therefore $$44100 \times 30 \times 2 = 2.646\text{ MB}$$. This is too large for on-chip SRAM but well within the GIGA's 8 MB of external SDRAM.

### USB-Injected Noise

Whenever a high-speed digital interface like USB Full-Speed (12 Mbps) shares a PCB with a sensitive analog circuit, layout becomes the dominant factor in noise performance. The audible artifact is usually a high-pitched whine or buzz that tracks USB activity. This is fundamentally a property of the Arduino GIGA R1 itself, not something the SensEdu shield can fix.

Two coupling mechanisms are typically at play:

- **Ground-return coupling**: return currents from the USB lines flow through the ground plane shared with the ADC, producing a small voltage drop across the finite resistance and inductance of the plane. The analog input, which references the same ground, sees that drop as common-mode noise.
- **Capacitive coupling**: parasitic capacitance between adjacent USB and analog traces lets some USB signal couple directly into the analog trace, where it appears as a voltage glitch.

A look at the official [GIGA R1 schematics](https://docs.arduino.cc/resources/schematics/ABX00063-schematics.pdf) confirms that analog and digital grounds are not separated, which is what an audio-focused board would do differently. A full investigation of the problem would require an analysis of PCB files [here](https://docs.arduino.cc/static/5927a4ebbe3f363ebd68e7c50de5e0af/ABX00063-cad-files.zip).

Since we can't change the hardware, the firmware works around it. The classical "stream every sample as it arrives" architecture spreads this noise uniformly through the recording. An example of such a recording:

<audio controls preload="metadata">
  <source src="{{site.baseurl}}/assets/audio/continuous-usb-stream.opus" type="audio/ogg; codecs=opus">
  Audio rendering failed.
</audio>

For better visualization, I connected a sinusoid from a signal generator to the input. The signal is sampled with parallel USB requests at the beginning of each DMA half-buffer. Orange circles on the plot separate these "segments". USB transfers are visible as high-frequency bursts of noise at the beginning of each half-buffer.

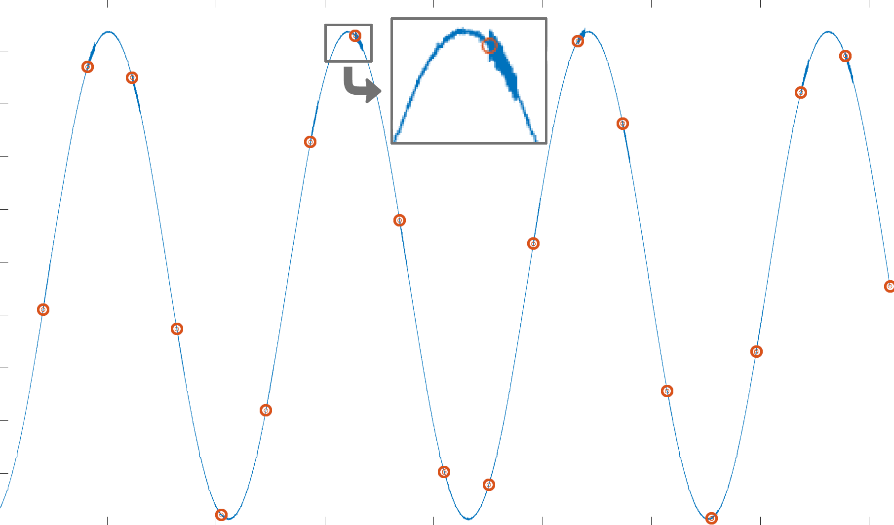
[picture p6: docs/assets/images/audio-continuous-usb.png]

{: .text-center}

This issue is the reason why a **batched transfers** architecture is used instead. The firmware records audio into SDRAM with no concurrent USB activity, then dumps a whole SDRAM segment over USB at once. The audible result is that the noise is confined to short bursts between much larger segments, leaving the rest of the audio clean. See [SDRAM Slot Ring](#sdram-slot-ring) and [Transfer Pipeline](#transfer-pipeline) for how this is implemented.

## Code Layout

The firmware is a single `.ino` file and the host is a single `.m` file. Everything lives under `projects/Audio_Recording/`.

| File | Purpose |
|---|---|
| `Audio_Recording.ino` | Entry point. ADC + DMA + SDRAM setup, command parser, capture pipeline, USB transfer pipeline. |
| `matlab/Audio_Recording.m` | Host script. Opens the serial port, drives the start/stop handshake, reads framed segments, saves the WAV file, plots waveform + FFT. |

## Configuration

All tunable constants live at the top of `Audio_Recording.ino`:

| Constant | Default | Meaning |
|---|---|---|
| `SAMPLING_RATE` | 44100 | ADC sampling rate in Hz. |
| `CHUNK_SIZE` | 256 | DMA half-buffer size in samples. |
| `SEGMENT_SECONDS` | 30 | Length of each SDRAM slot. Each slot consumes `SAMPLING_RATE × SEGMENT_SECONDS × 2` bytes. |
| `SEGMENT_NUM` | 2 | Number of SDRAM slots in the ping-pong. Total SDRAM footprint = `SEGMENT_NUM` × per-slot bytes; must stay under 8 MB. |
| `USB_CHUNK_BYTES` | 4080 | Payload bytes per `Serial.write` call. Deliberately not a multiple of 64; see [USB Short Packet](#usb-short-packet). |

On the MATLAB side:

| Variable | Default | Meaning |
|---|---|---|
| `ARDUINO_PORT` | `'COM16'` | GIGA serial port. |
| `RECORDING_DURATION_SEC` | 40 | Desired recording length. The host requests `ceil(duration / SEGMENT_SECONDS)` segments and trims the excess. |
| `ENABLE_PLAYBACK` | `true` | Auto-play the recording when the script finishes. |

## Firmware Implementation

This section describes the general idea behind the firmware implementation. Refer to the full source under `projects/Audio_Recording/` for the complete picture.

### State Machine

The firmware lives in one of two states:

* `STATE_IDLE` – ADC is OFF, no slots are filling, no data is being transmitted. Default after boot.
* `STATE_RECORDING` – ADC is ON, DMA is filling the SRAM ping-pong, and the main loop is copying samples to SDRAM and (when a slot fills) transmitting them.

Transitions are driven by host commands, covered in [Session Lifecycle](#session-lifecycle). The main loop itself is non-blocking and stateless beyond these two states:

```c
void loop() {
    process_command();
    process_capture();
    process_usb_transfer();
}
```

{: .NOTE}
Each function does at most one unit of work per iteration. The loop never blocks on long operations.

### SDRAM Slot Ring

The Arduino GIGA's on-chip SRAM is too small for the multi-megabyte recordings we are targeting, so the slots live in the GIGA's external 8 MB SDRAM. Each slot has its own buffer plus metadata.

```c
typedef struct {
    uint16_t* buffer;        // SDRAM buffer pointer (allocated once at boot, never freed)
    uint32_t  sequence_id;   // 0-based id within the current firmware session
    uint32_t  sample_count;  // Valid sample count in this slot
    uint32_t  flags;
    bool      ready;
} Slot;

static Slot slots[SEGMENT_NUM];
```

Buffers are allocated once at boot via the bundled `SDRAM` library and never freed for the rest of the program's life. This is the only dynamic allocation in the whole firmware:

```c
static bool allocate_sdram() {
    for (uint8_t i = 0; i < SEGMENT_NUM; i++) {
        slots[i].buffer = (uint16_t*)SDRAM.malloc(SEGMENT_BYTES);
        if (slots[i].buffer == NULL) {
            return false;
        }
    }
    return true;
}
```

The `slots[]` array is then treated as a **ring**, with two state structs tracking the producer (capture) and consumer (transfer) sides independently:

```c
typedef struct {
    uint8_t  write_idx;         // Currently filling slot
    uint32_t captured_samples;  // Samples written into the current slot so far
    uint32_t next_sequence_id;  // Next id to assign on slot completion
} CaptureState;

typedef struct {
    int8_t   slot_idx;     // Slot being transmitted (NO_SLOT if none)
    uint32_t bytes_sent;   // Payload bytes already sent for the current slot
    bool     header_sent;  // Header already sent for the current slot
    bool     tail_sent;    // Tail magic already sent for the current slot
} TransferState;
```

* **Capture side** (`CaptureState`) writes into `slots[capture.write_idx]`. When the slot fills it sets `ready = true` and advances to the next index.
* **Transfer side** (`TransferState`) picks whichever slot has `ready == true` and the lowest `sequence_id`, transmits it, then sets `ready = false`.

The `ready` flag is the only synchronization between the two sides.

### Capture Pipeline

`process_capture` polls the two DMA flags. Whenever either fires, it copies the corresponding half of the SRAM ping-pong into the current SDRAM slot:

```c
static void process_capture() {
    if (fw_state != STATE_RECORDING) return;

    if (SensEdu_ADC_IsDmaHalfTransferComplete(adc)) {
        SensEdu_ADC_ClearDmaHalfTransferComplete(adc);
        save_dma_half(&dma_buf[0], DMA_BUF_SIZE / 2);
    }
    if (SensEdu_ADC_IsDmaTransferComplete(adc)) {
        SensEdu_ADC_ClearDmaTransferComplete(adc);
        save_dma_half(&dma_buf[DMA_BUF_SIZE / 2], DMA_BUF_SIZE / 2);
    }
}
```

`save_dma_half` is where the slot ring actually advances. A 256-sample DMA half-buffer almost never divides the slot size evenly, so the same call that finishes one slot also has to begin filling the next one:

```c
static void save_dma_half(volatile uint16_t* src, uint16_t src_length) {
    uint16_t copied = 0;
    while (copied < src_length) {
        if (slots[capture.write_idx].ready) {
            pending_overrun_flag |= FLAG_OVERRUN_DROPPED;
            return;
        }

        uint16_t* dst = slots[capture.write_idx].buffer;
        uint32_t remaining_in_slot = SEGMENT_SAMPLES - capture.captured_samples;
        uint32_t to_copy = (uint32_t)(src_length - copied);
        if (to_copy > remaining_in_slot) {
            to_copy = remaining_in_slot;
        }

        for (uint32_t i = 0; i < to_copy; i++) {
            dst[capture.captured_samples + i] = src[copied + i];
        }
        capture.captured_samples += to_copy;
        copied += (uint16_t)to_copy;

        if (capture.captured_samples >= SEGMENT_SAMPLES) {
            mark_slot_ready();
        }
    }
}
```

`mark_slot_ready` hands the just-filled slot off from the capture side to the transfer side. Once `ready` flips to `true`, the next call to `process_usb_transfer` is free to pick it up.

```c
static void mark_slot_ready() {
    uint8_t idx = capture.write_idx;
    slots[idx].sequence_id  = capture.next_sequence_id++;
    slots[idx].sample_count = SEGMENT_SAMPLES;
    slots[idx].flags        = pending_overrun_flag;
    slots[idx].ready        = true;
    pending_overrun_flag    = 0;

    capture.captured_samples = 0;
    capture.write_idx = (uint8_t)((idx + 1) % SEGMENT_NUM);
}
```

#### Slot Overrun

If the host stalls for long enough that the next SDRAM slot isn't yet free when capture needs it, the firmware drops the incoming DMA samples and sets `FLAG_OVERRUN_DROPPED` so that the next emitted header carries a "samples were lost before this segment" notice. The host warns the user and keeps going. Dropping rather than halting keeps the firmware recoverable.

```c
if (slots[capture.write_idx].ready) {
    pending_overrun_flag |= FLAG_OVERRUN_DROPPED;
    return;
}
```

### Transfer Pipeline

Once a slot is `ready`, `process_usb_transfer` sends a 20-byte header, then the raw sample bytes in `USB_CHUNK_BYTES` pieces, and finally an 8-byte trailer. The trailer acts as a framing integrity check; see [Why a Segment Tail](#why-a-segment-tail) for the details.

The slot to transmit is chosen by lowest `sequence_id`, not by lowest index, because the host validates strict sequence ordering on every header:

```c
int8_t best = NO_SLOT;
uint32_t best_seq = 0;
for (uint8_t i = 0; i < SEGMENT_NUM; i++) {
    if (!slots[i].ready) continue;
    if (best == NO_SLOT || slots[i].sequence_id < best_seq) {
        best = (int8_t)i;
        best_seq = slots[i].sequence_id;
    }
}
```

Header and trailer each have their own struct and magic word (a fixed constant both sides agree on to confirm frame alignment), so the host can verify framing and integrity immediately on arrival:

```c
typedef struct {
    uint32_t magic;
    uint32_t session_id;
    uint32_t sequence_id;
    uint32_t sample_count;
    uint32_t flags;
} SegmentHeader;

typedef struct {
    uint32_t magic;
    uint32_t sequence_id;
} SegmentTail;
```

### Session Lifecycle

For clean restarts from the host, every new session needs a clean firmware state. `reset_pipeline` zeroes every ring index, slot flag, and transfer cursor. It does not touch the SDRAM buffer pointers or the `session_id`:

```c
static void reset_pipeline() {
    for (uint8_t i = 0; i < SEGMENT_NUM; i++) {
        slots[i].ready = false;
        slots[i].sequence_id = 0;
        slots[i].sample_count = 0;
        slots[i].flags = 0;
    }
    capture.write_idx = 0;
    capture.captured_samples = 0;
    capture.next_sequence_id = 0;
    transfer.slot_idx = NO_SLOT;
    transfer.bytes_sent = 0;
    transfer.header_sent = false;
    transfer.tail_sent = false;
    pending_overrun_flag = 0;
}
```

Host commands drive the state transitions. The `'s'` command invokes `cmd_start`, which brings the firmware into a clean recording state regardless of what it was doing before:

```c
static void cmd_start() {
    SensEdu_ADC_Disable(adc);
    SensEdu_ADC_ClearDmaTransferComplete(adc);
    SensEdu_ADC_ClearDmaHalfTransferComplete(adc);

    reset_pipeline();
    session_id++;
    fw_state = STATE_RECORDING;

    send_ack('s', 0);

    SensEdu_ADC_Enable(adc);
    SensEdu_ADC_Start(adc);
}
```

{: .NOTE}
`session_id` is incremented on every start. The host captures the new value from the start ACK and validates it on every subsequent frame, so any leftover data from a prior session is rejected automatically.

{: .WARNING}
The ACK is emitted **before** the ADC is re-enabled. If the ADC were running while the ACK was being written, a slow `Serial.write` could let the first DMA half-buffer fill and be overwritten, even before the main loop got a chance to drain it.

The `'p'` command invokes `cmd_stop`, which brings the firmware back to idle. It also reports the number of completed segments in the ACK's `info` field for the host's own logging:

```c
static void cmd_stop() {
    if (fw_state == STATE_RECORDING) {
        SensEdu_ADC_Disable(adc);
        fw_state = STATE_IDLE;
    }

    uint32_t segments_completed = capture.next_sequence_id;
    reset_pipeline();
    send_ack('p', segments_completed);
}
```

The `'?'` command is a status query. The ACK carries the current state and the number of samples already captured into the active slot:

```c
static void cmd_status() {
    send_ack('?', capture.captured_samples);
}
```

## MATLAB Host

The host script is located at `projects/Audio_Recording/matlab/Audio_Recording.m`. It opens the serial port, drives the start/stop handshake, reads framed segments into a buffer, saves the result as a WAV file, and plots the waveform and magnitude spectrum.

### Restart-Safe Handshake

After opening the serial port, the script sends `'p'` to bring the firmware to a known idle state. This works regardless of what the firmware was doing: finishing a transfer from a previous run, mid-recording, or idle. Then `'s'` starts a fresh session and the start ACK carries the new `session_id`:

```matlab
write(arduino, uint8('p'), 'uint8');
read_ack(arduino, 'p', FIRST_ACK_WAIT_SEC, RESYNC_MAX_BYTES, ACK_MAGIC, ACK_BYTES);

write(arduino, uint8('s'), 'uint8');
start_ack  = read_ack(arduino, 's', ACK_WAIT_SEC, ACK_BYTES * 2, ACK_MAGIC, ACK_BYTES);
session_id = start_ack.session_id;
```

### Framed Reading

Every frame from the firmware is read through a single helper, `read_framed`, that locates the magic word and applies a per-frame validator:

1. Read `frame_bytes` from the port.
2. If the first 4 bytes match the magic *and* the validator accepts the frame, return it.
3. Otherwise, slide forward looking for the magic; repeat. Abort once `max_resync_bytes` have been scanned.

The validator performs the structural sanity check:
- For segment headers: requires `session_id` to match the active session and `sample_count` to be within bounds
- For ACKs: requires `cmd` to be the one we just sent

```matlab
function ok = seg_is_valid(buf, expected_session_id, max_samples)
    session_id   = typecast(uint8(buf(5:8)),   'uint32');
    sample_count = typecast(uint8(buf(13:16)), 'uint32');
    flags        = typecast(uint8(buf(17:20)), 'uint32');
    ok = (session_id == expected_session_id) && (sample_count > 0) ...
         && (sample_count <= max_samples) && (flags <= 1);
end

function ok = ack_is_valid(buf, expected_cmd)
    cmd_char = char(buf(5));
    state = buf(6);
    pad = typecast(uint8(buf(7:8)), 'uint16');
    ok = (cmd_char == expected_cmd) && (state == 0 || state == 1) && (pad == 0);
end
```

The `read_framed` implementation reads the stream in 64 KB chunks (defined by `SCAN_CHUNK`) and locates the magic with a `find_pattern` byte-search helper.

### Segment Receive Loop

With the session live, the host requests `SEGMENTS_TO_RECORD` audio segments. Each iteration reads the three pieces in order: header, payload, and tail; verifies the header and tail, and saves the payload by copying it into the `data_full` buffer:

```matlab
for seg = 1:SEGMENTS_TO_RECORD
    hdr = read_segment_header(arduino, HEADER_WAIT_SEC, RESYNC_MAX_BYTES, ...
                              SEG_MAGIC, SEG_HDR_BYTES, session_id, SEGMENT_SAMPLES);

    if double(hdr.sequence_id) ~= (last_seq_id + 1)
        partial_recording = true;  break;     % sequence gap, keep what we have
    end
    last_seq_id = double(hdr.sequence_id);

    samples = read_samples(arduino, double(hdr.sample_count), PAYLOAD_WAIT_SEC);
    tail_ok = read_segment_tail(arduino, PAYLOAD_WAIT_SEC, SEG_TAIL_MAGIC, ...
                                SEG_TAIL_BYTES, hdr.sequence_id);

    data_full(write_pos + 1 : write_pos + numel(samples)) = samples;
    write_pos = write_pos + numel(samples);

    if ~tail_ok
        partial_recording = true;  break;     % stream drift, keep what we have
    end
end
```

When the `sequence_id` jumps or the tail magic doesn't match, the loop breaks and the script saves whatever it captured so far. See [Why a Segment Tail](#why-a-segment-tail) for why the tail check matters.

### Saving and Plotting

After the loop, the host sends `'p'` to stop the session and trims `data_full` to either `write_pos` (what was actually captured) or `RECORDING_DURATION_SEC * Fs` (the requested length), whichever is smaller. If any segments carried `FLAG_OVERRUN_DROPPED` or the recording ended early, a warning is printed before saving.

The 16-bit unsigned ADC samples are then normalized to the `[-1, +1]` range that `audiowrite` expects, and the residual DC bias from the microphone preamp is subtracted:

```matlab
y = data_full / 65535;
y = 2 * y - 1;
y = y - mean(y);
audiowrite(file_name, y, Fs);
```

The file is written to `Recordings/recorded_audio_<timestamp>.wav`, and the script finally plots the time-domain waveform and the magnitude spectrum (and optionally plays the result if `ENABLE_PLAYBACK` is set).

## Stability
Before the showcase, we should address the elephant in the room – the sheer number of handshakes, checks, and guards in the firmware and host.

The USB data transfer between the Arduino GIGA R1 and MATLAB is not something we designed, and it is not really suited for this application. It uses general-purpose USB CDC, which by design is allowed to drop bytes when the host is busy or stalls, thus very awkward to deal with for a real-time application like audio recording. In other projects we never minded the occasional dropped bytes since only the last small chunk of data really mattered. But here, the audio is a long, continuous stream that is expected to be perfectly uninterrupted.

This is easy to see for yourself – try running the host script with MATLAB being the only running software and as the current active window. Just sit and wait; it should complete reliably almost every single time, without any warnings.

Afterwards, try starting the script while browsing the web, watching a video, or copying some files. You'll see the script throw warnings far more often.

All the handshakes exist to ensure that dropped bytes are detected and handled cleanly, so the data that was successfully acquired is still saved, and the application can be restarted smoothly.

## Showcase

Segment length is set to 30 seconds for these recordings. You should hear a brief USB-injected noise at each segment boundary.

### Ambient

Recorded on the balcony on a summer day.

<audio controls preload="metadata">
  <source src="{{site.baseurl}}/assets/audio/recording-ambient.opus" type="audio/ogg; codecs=opus">
  Audio rendering failed.
</audio>

### Music

[Hod Battle](https://youtu.be/83vTbIzGZ4Y?si=8hvAV47SZglAqdIQ) from [Library of Ruina](https://store.steampowered.com/app/1256670/Library_Of_Ruina/) playing about 40 cm from the board at a 90° angle, through a Bluetooth speaker.

<audio controls preload="metadata">
  <source src="{{site.baseurl}}/assets/audio/recording-music.opus" type="audio/ogg; codecs=opus">
  Audio rendering failed.
</audio>

### Voice

[Voice lines of Andre the Blacksmith](https://youtu.be/kWtMg9w9rhc?si=zD7kksJOjzZmQwnT) from [Dark Souls III](https://store.steampowered.com/app/374320/DARK_SOULS_III/) playing about 40 cm from the board at a 90° angle, through a Bluetooth speaker.

<audio controls preload="metadata">
  <source src="{{site.baseurl}}/assets/audio/recording-voice.opus" type="audio/ogg; codecs=opus">
  Audio rendering failed.
</audio>

## Developer Notes

### USB Short Packet

The Windows USB CDC (Communications Device Class) driver delivers bulk data only when one of three things happens: 
- Driver's read buffer fills (typically 4096 B)
- **Short packet** (< 64 B) arrives
- Read timeout expires

If every `Serial.write` is an exact multiple of 64 B, no short packet is ever produced and trailing bytes sit in the driver's buffer until the read times out.

**Firmware must use sizes that are not a multiple of 64 B to end with a short packet**

```c
static const uint32_t USB_CHUNK_BYTES = 4080;   // 63 * 64 + 48
```

The trailing 48-byte chunk is the short packet that flushes the buffer.

{: .WARNING}
`Serial.flush()` does not help.

### Why a Segment Tail

The segment header alone is enough to *frame* the payload (the host knows how many bytes to read from `sample_count`), but it cannot *verify* that the firmware and host agree on the byte count. 

If the firmware ever sends fewer or more bytes than the header announced, the host's blocking read would silently consume the wrong bytes and the misalignment would only surface later as a corrupted next header or a sequence-id discontinuity. The trailer turns this silent drift into an immediate, localized failure.

On mismatch the host emits a warning, stops the loop, trims `data_full` to whatever was successfully captured, and saves the partial WAV.

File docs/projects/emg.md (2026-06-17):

---
title: EMG BioInputs
layout: default
parent: Projects
math: mathjax
nav_order: 7
---

# EMG BioInputs
{: .fs-8 .fw-500 .no_toc}
---

- TOC
{:toc}

## Introduction

[Electromyography](https://en.wikipedia.org/wiki/Electromyography) (EMG) is a widely-used technique for recording and analyzing electrical activities generated by skeletal muscles.

EMG is appealing due to its simplicity when detecting basic movements, such as a biceps contraction. For such projects, advanced hardware or complex signal processing is often unnecessary. This makes EMG an accessible tool for beginners as an introduction to biomedical engineering projects. Furthermore, the foundational concepts learned through EMG can be extended to related fields, including [Electrocardiography](https://en.wikipedia.org/wiki/Electrocardiography) (ECG), [Electrooculography](https://en.wikipedia.org/wiki/Electrooculography) (EOG), [Electroencephalography](https://en.wikipedia.org/wiki/Electroencephalography) (EEG), and others.

In SensEdu, we demonstrate how basic biceps contraction can be used to simulate keyboard press logic, with latency of ~100 ms. We use the most basic circuit design combined with signal processing in MATLAB.

This page will guide you step-by-step through the setup and background knowledge to create a simple yet effective demonstration of a typical biomedical engineering project.

## Biological Background

First, we need to establish an understanding of what we are trying to measure.

{: .TIP}
It is highly recommended watching the video [Neuromuscular Junction](https://youtu.be/_k6QINRcdV4?si=TG5Yw0wvDcTJtR6G) by [Byte Size Med].

The most important structure that we need to focus on is the [Neuromuscular Junction](https://en.wikipedia.org/wiki/Neuromuscular_junction) (NMJ). This is a specialized [synapse](https://en.wikipedia.org/wiki/Synapse) that acts as a communication bridge between [motor neurons](https://www.simplypsychology.org/motor-neuron.html) and skeletal muscle fibers. The NMJ plays a fundamental role in converting neural signals into muscle contraction. Let's break down its working principle step by step.

The process begins with a motor neuron transmitting an electrical signal called an [Action Potential]. This signal travels along neuron's [axon](https://en.wikipedia.org/wiki/Axon) until it reaches the NMJ. It activates **voltage-gated sodium channels**, which allow positively charged sodium ions (Na⁺) to enter the cell. The influx of sodium causes the cell membrane to become *"less negatively charged"*, a change known as **depolarization**.

Continuous depolarization of the cell membrane subsequently activates **voltage-gated calcium channels**. Calcium ions (Ca²⁺) flow into the cell, triggering [little containers](https://en.wikipedia.org/wiki/Synaptic_vesicle) with [neurotransmitters](https://en.wikipedia.org/wiki/Neurotransmitter) to fuse with the membrane and release [Acetylcholine](https://en.wikipedia.org/wiki/Acetylcholine) (ACh).


{: .text-center .mb-1}

[Exocytosis](https://en.wikipedia.org/wiki/Exocytosis) process at the Neuromuscular Junction (source: [Byte Size Med])
{: .text-center .mt-0 .fw-500}

Acetylcholine travels across the synaptic space and binds to specialized receptors on the muscle cell's membrane. These receptors, also known as [ligand-gated ion channels](https://en.wikipedia.org/wiki/Ligand-gated_ion_channel), respond to the chemical messenger (neurotransmitter) by opening and allowing ions to enter the muscle cell. This process triggers membrane **depolarization**, causing the resting membrane potential of the muscle cell (normally at around -90mV) to become less negative.


{: .text-center .mb-1}

[Depolarization](https://en.wikipedia.org/wiki/Depolarization) caused by the opening of ligand-gated ion channels (source: [Byte Size Med])
{: .text-center .mt-0 .fw-500}

As more ACh molecules bind to their receptors, the membrane voltage continues to rise. Once it reaches a threshold of approximately -50 mV, **voltage-gated sodium channels** open, allowing sodium ions (Na⁺) to rush into the muscle cell. This influx of sodium completes the process of membrane depolarization and generates an **Action Potential**. This electrical signal propagates along the muscle membrane, eventually leading to a muscle contraction.


{: .text-center .mb-1}

[Excitation-Contraction Coupling](https://www.sciencedirect.com/topics/medicine-and-dentistry/excitation-contraction-coupling) (source: [Byte Size Med])
{: .text-center .mt-0 .fw-500}

{: .NOTE}
If you feel overwhelmed by the details, the main takeaway: a neural electrical signal is converted to a chemical signal and then back into electrical signal in the muscle. The sequence is: **Neural Action Potential** → **Acetylcholine Release** → **Muscle Action Potential**. The muscle action potential then propagates along the muscle cell membrane and ultimately triggers muscle contraction. The most important point is that this **muscle action potential can be measured**, providing valuable information about muscle activity.

## Recording Action Potentials

Action Potentials can be recorded using different methods:
* **Invasive Needle EMG**: Inserting electrodes directly into the muscle, enabling highly precise and localized recordings. It is widely used in clinical applications and treatments where precision and measurement quality are critical.
* **Non-invasive Surface EMG**: Placing electrodes on the skin above the muscle. This approach improves patient comfort and simplifies repeatable studies, making it ideal for educational purposes. However, sEMG has significant precision **limitations due to the layers of skin and fat** between the electrodes and the muscle. These limitations make it challenging to differentiate the activity of individual muscle fibers and to record signals from small muscles, such as those around the fingers.

{: .NOTE}
In SensEdu we use surface EMG. From now on, whenever we mention EMG or electrodes, we are referring to sEMG and surface electrodes, respectively.

## Hardware Setup

This section describes the necessary connections and hardware details required for the proper setup of the EMG BioInputs system and writing the script for the MCU. Below is an illustration of the overall system architecture.

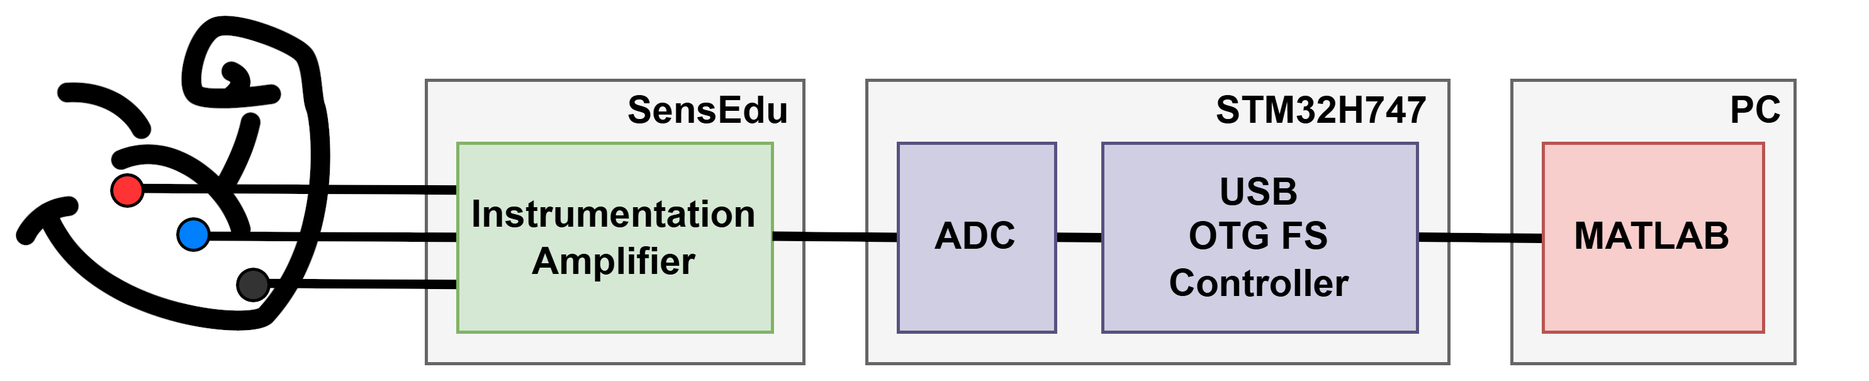
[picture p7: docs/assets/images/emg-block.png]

{: .text-center .mb-1}

EMG BioInputs System Architecture
{: .text-center .mt-0 .fw-500}

### Electrodes Connectivity

The system supports **up to 4 EMG probes**, which can be connected via female 4-Pin 2.54 headers: **J8**, **J9**, **J10**, and **J11**. 

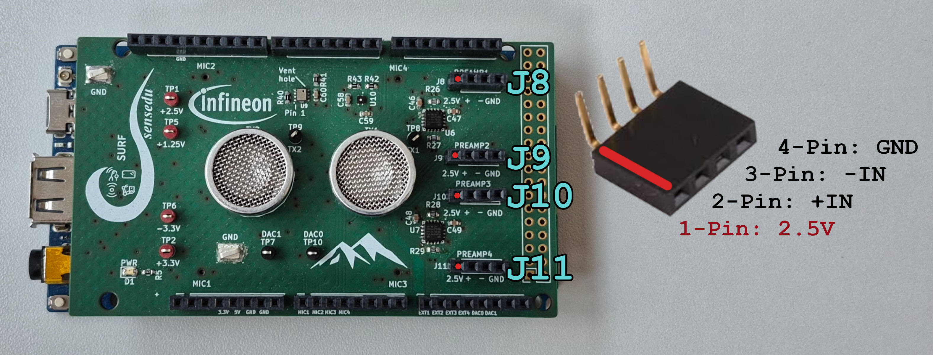
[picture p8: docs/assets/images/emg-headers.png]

{: .text-center .mb-1}

SensEdu input headers (red dots mark the 1st pin)
{: .text-center .mt-0 .fw-500}

A typical electrode consists of 3 connectors: **Reference**, **Positive Input**, and **Negative Input**. Below is a table detailing how these connectors correspond to the pins on the headers. Note that the voltage pin (1st pin) on the headers is not used in this connection.

| Electrode Connector | Signal | Header Pin |
|:--------------------|:-------|:-----------|
| Positive Input      |   +IN  | 2nd Pin    |
| Negative Input      |   –IN  | 3rd Pin    |
| Reference           |   GND  | 4th Pin    |

{: .WARNING}
Most commercially available electrodes use connectors that are not directly compatible with typical 2.54 headers. For your specific electrode, you will need a way to make this connection work via soldering, custom adapters, or ready-made solutions.

In our example, we used the following electrodes:

| Manufacturer | Product Title | Product Code | Datasheet | Store |
|:-------------|:--------------|:-------------|:----------|:------|
| SparkFun Electronics | Electrode Pads | 12970 | [link](https://mm.digikey.com/Volume0/opasdata/d220001/medias/docus/2277/CAB-12970_Web.pdf) | [link](https://www.digikey.at/de/products/detail/sparkfun-electronics/12970/6833933?gclsrc=aw.ds&gad_source=1&gad_campaignid=20265439570&gclid=CjwKCAjwqKzEBhANEiwAeQaPVawVKSgXTIiVYtlIXGx7Bx94wvNKO64lkmGlu8jQ0lByNxnXmPGLFhoCgNcQAvD_BwE) |
| MTG Imiella Medizintechnik | Liquid Gel Disposable Electrodes for ECG (Ø 40mm) | S40LG | [link](https://static.mercateo.com/ec/2c36d66dd9904e92ad9e3075734affb2/pdf/106366.pdf?v=2297) | [link](https://www.mercateo.at/p/2768-028002/Einmal_Klebeelektroden_40_mm_Liquid_Gel_30_Stueck.html) |

These electrodes use a mini-jack connector. To simplify the connection, we designed a simple PCB adapter **MiniJack2Header**. This adapter is inserted vertically into the SensEdu header, providing a mini-jack socket and eliminating the need for soldering. All PCB source files, including Gerbers and BOM, are available in the directory: `/projects/EMG-BioInputs/pcbs/MiniJack2Header`. To replicate our setup, you can use the archive `MiniJack2Jumper/manufacturing/MiniJack2Header-Gerber.zip` to order the PCB. For this simple adapter you can use any cheap manufacturer, with the final cost typically ranging from $15–$30 depending on shipping.

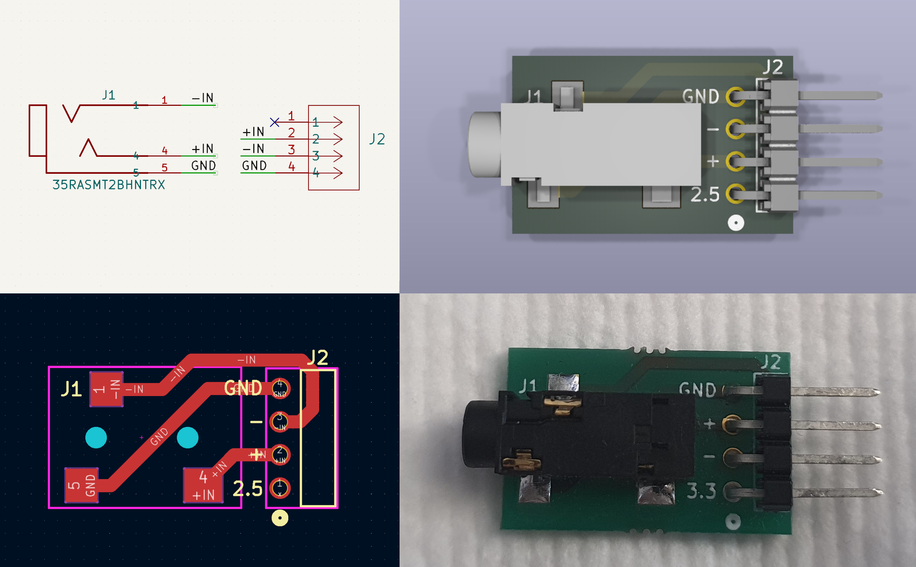
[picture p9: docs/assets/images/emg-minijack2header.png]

{: .text-center .mb-1}

MiniJack2Header adapter: Schematics, PCB view, 3D view, and real-life view
{: .text-center .mt-0 .fw-500}

After connecting the electrodes using the MiniJack2Header adapter, the final setup looks as follows:


{: .text-center .mb-1}

Electrode connection to SensEdu
{: .text-center .mt-0 .fw-500}

### Amplifier Circuit

The first stage after the input electrodes is signal amplification. 

The idea is to detect a signal at two points, amplify the "difference", and remove everything "common" between them. This way, the local EMG signal will be isolated and amplified. For that, we need a differential amplifier with a **high Common Mode Rejection Ratio** (CMRR), at least 90 dB. 

Besides CMRR, an amplifier must also have a **high input impedance**. The impedance of the electrode-skin interface can vary from several thousand ohms to several megohms for dry skin. To prevent attenuation and distortion of the detected signal due to input loading, the input impedance of the differential amplifier should be as large as possible.

A differential amplifier with input buffer amplifiers, which features very high CMRR and input impedance, is called an [Instrumentation Amplifier](https://en.wikipedia.org/wiki/Instrumentation_amplifier). SensEdu is equipped with this type of amplifiers, specifically the x2 dual-channel [AD8426](https://www.analog.com/media/en/technical-documentation/data-sheets/AD8426.pdf), making the platform suitable for biosignal measurements.

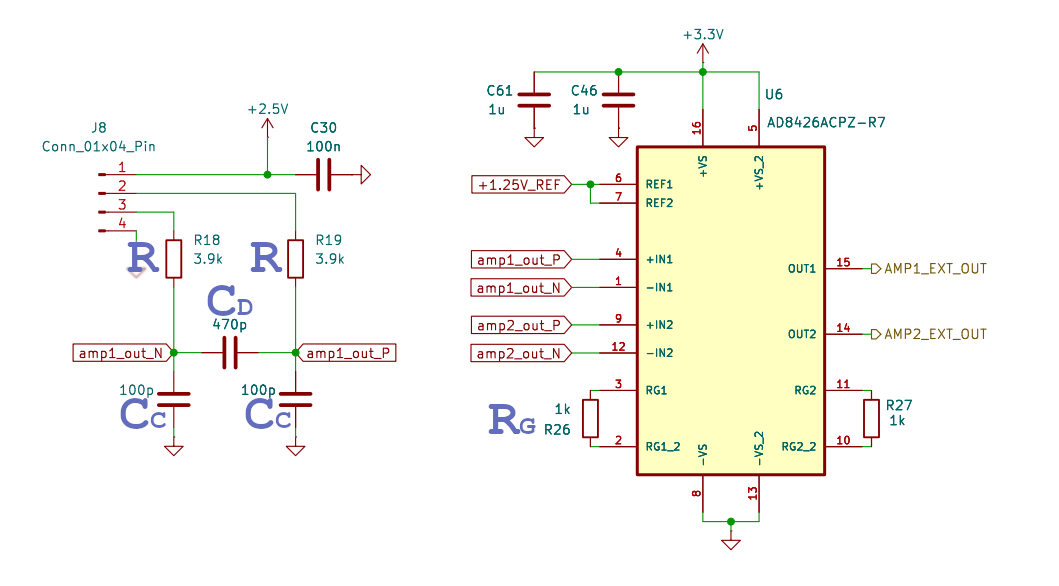
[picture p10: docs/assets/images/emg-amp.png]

{: .text-center .mb-1}

Amplification Circuit
{: .text-center .mt-0 .fw-500}

Gain is set by the $$R_G$$ resistor, using the following formula:

$$G = 1 + \frac{49.4\text{ kΩ}}{R_G} = 1 + \frac{49.4\text{ kΩ}}{1\text{ kΩ}} = 50.4$$

To avoid high frequency rectification and thus signal distortions, additional filtering is applied at the input. The filter limits the input signal bandwidth according to the following relationships:

$${f_c}_{DIFF} = \frac{1}{2\pi × R(2C_D + C_C)} = \frac{1}{2\pi × 3.9\text{ kΩ}(2×470\text{ pF} + 100\text{ pF})} = 37.7\text{ kHz}$$

$${f_c}_{CM} = \frac{1}{2\pi × R × C_C} = \frac{1}{2\pi × 3.9\text{ kΩ} × 100\text{ pF}} = 392.2\text{ kHz}$$

{: .NOTE}
Mismatch between $$R \times C_C$$ at the positive and negative inputs degrades the CMRR of the AD8426. By using a value for $$C_D$$ that is ~10× larger than $$C_C$$, the effect of the mismatch is reduced and performance is improved.

We used the default $${f_c}_{DIFF}$$ and $${f_c}_{CM}$$ cutoff frequencies for all projects, which were originally selected to suit the ultrasonic use case. Additional optimization is possible by reducing these cutoff frequencies to align with the working range of EMG signals (up to ~$$500\text{ Hz}$$). It could result in improved signal quality and reduced post‐processing requirements.

To write Arduino scripts for EMG signal acquisition, it is crucial to understand how the amplifier I/O is wired. Specifically, the following details:
* Which input header is connected to each amplifier channel
* Which amplifier output corresponds to which ADC channel on the MCU

All these details are available in the [SensEdu schematics]({{site.baseurl}}/assets/pdf/schematics.pdf) and [ADC mapping table]({% link library/adc.md %}#adc_mapping). For convenience, the table below provides a summary of the relevant connections:

#### SensEdu 0.7
{: .no_toc}

| Input Header | Amplifier Channel | Output Arduino Pin | Output STM32 Pin | Available ADCs
|:------|:--------|:------|:------|:------------|
| J9    | U5 CH1  | A0    | PC4   | ADC1 & ADC2 |
| J11   | U5 CH2  | A2    | PB0   | ADC1 & ADC2 |
| J12   | U6 CH1  | A11   | PA0_C | ADC1 & ADC2 |
| J20   | U6 CH2  | A7    | PA0   | ADC1        |

#### SensEdu 0.8+
{: .no_toc}

| Input Header | Amplifier Channel | Output Arduino Pin | Output STM32 Pin | Available ADCs
|:------|:--------|:------|:------|:------------|
| J8    | U6 CH1  | A8    | PC2_C | ADC3        |
| J9    | U6 CH2  | A9    | PC3_C | ADC3        |
| J10   | U7 CH1  | A10   | PA1_C | ADC1 & ADC2 |
| J11   | U7 CH2  | A11   | PA0_C | ADC1 & ADC2 |

{: .NOTE}
`PC2_C (A8)` and `PC3_C (A9)` can be shorted to their non-C pins, `PC2 (A5)` and `PC3 (A4)` respectively. This lets a signal entering the C-pin connector be read through the ADCs available on the corresponding non-C pin. To do that, the SensEdu Library provides the `SensEdu_ADC_ShortA4A9()` and `SensEdu_ADC_ShortA5A8()` calls.

### Data Acquisition

The next step is to develop the Arduino sketch responsible for data acquisition. This involves configuring ADC parameters, such as sampling rate, buffer size, memory mode, etc.

For EMG, a sampling rate of $$1\text{ kHz}$$ is the minimum requirement. To improve the quality of signal acquisition, this project uses a higher value of $$f_s = 5\text{ kHz}$$. Each channel uses a buffer of $$N_s = 75 \ \text{samples}$$. ADC is configured with circular DMA to minimize CPU load and maximize performance. The ideal theoretical duration of one measurement chunk is given as:

$$d_{chunk, \ ideal} = \frac{N_s}{f_s} = \frac{75 \ \text{samples}}{5\text{ kHz}} = 15\text{ ms} $$

{: .NOTE}
The measurement duration is calculated for one channel. If you use multiple channels and intend to maintain the same measurement chunk, **do not change the sampling rate**, it is shared across all channels. You need only to increase the DMA buffer size.

In practice, the actual $$d_{chunk}$$ considering data transmission is approximately $$16\text{ ms}$$, it will be measured in the next [Data Transfer]({% link projects/emg.md %}#data-transfer) section.

Keeping the selected parameters in mind, the ADC can be configured using the [SensEdu Library]({% link library/index.md %}). The configuration follows a similar structure to the [ADC_3CH_DMA_Circular]({% link library/adc.md %}#adc_3ch_dma_circular) example. Below is a minimal code example, focusing on the essentials. Code snippets show the EMG config for all x4 channels.

Since DMA is set to the circular mode, the optimal DMA buffer size should be small. The EMG chunk is planned as $$N_s = 75 \ \mathrm{samples}$$, so the size can simply be doubled so that a half-transfer holds exactly $$75$$ samples. Considering 4 channels, the final total DMA buffer size is: $$75 \times 2 \times 4 = 600$$ samples.

```c
// EMG Chunk Configuration
static const uint16_t EMG_CHUNK_SIZE = 75;

// ADC Settings
static ADC_TypeDef* adc = ADC1;
static const uint16_t SAMPLING_RATE_PER_CH = 5000;

static const uint16_t CHANNEL_NUM_PER_ADC = 4;
static uint8_t adc_pins[CHANNEL_NUM_PER_ADC] = {A5, A4, A10, A11};

// DMA Settings
static const uint16_t DMA_BUFFER_SIZE = EMG_CHUNK_SIZE * 2 * CHANNEL_NUM_PER_ADC;
volatile SENSEDU_DMA_BUFFER(dma_buffer, DMA_BUFFER_SIZE);

// Config Structure
SensEdu_ADC_Settings adc_settings = {
    .adc = adc,
    .pins = adc_pins,
    .pin_num = CHANNEL_NUM_PER_ADC,

    .sr_mode = SENSEDU_ADC_SR_MODE_FIXED,
    .sampling_rate_hz = SAMPLING_RATE_PER_CH,
    
    .adc_mode = SENSEDU_ADC_MODE_DMA_CIRCULAR,
    .mem_address = (uint16_t*)dma_buffer,
    .mem_size = DMA_BUFFER_SIZE
};
```

For simplicity, `ADC1` is used for all 4 channels. Since `A8` and `A9` have access only to `ADC3`, they are shorted to `A5` and `A4` respectively, making their signals readable through `ADC1`. Then, initialize, enable, and start the ADC.

```c
void setup() {
    Serial.begin(2000000);

    SensEdu_ADC_ShortA4A9();
    SensEdu_ADC_ShortA5A8();

    SensEdu_ADC_Init(&adc_settings);
    SensEdu_ADC_Enable(adc);
    SensEdu_ADC_Start(adc);
}
```

In the main loop, data is continuously recorded and transferred to the PC.

```c
void loop() {
    if (SensEdu_ADC_IsDmaHalfTransferComplete(adc)) {
        SensEdu_ADC_ClearDmaHalfTransferComplete(adc);
        transfer_buf(&dma_buffer[0], (DMA_BUFFER_SIZE / 2));
    }

    if (SensEdu_ADC_IsDmaTransferComplete(adc)) {
        SensEdu_ADC_ClearDmaTransferComplete(adc);
        transfer_buf(&dma_buffer[DMA_BUFFER_SIZE / 2], (DMA_BUFFER_SIZE / 2));
    }
}
```

The final expanded sketch is available at `/projects/EMG-BioInputs/EMG-BioInputs.ino`. It has some additional functionality, but the same core structure.

### Data Transfer

The GIGA R1 USB-C "Serial" port is a USB CDC (virtual COM port), not a hardware UART. As a result, the baud rate passed to `Serial.begin()` does not actually affect the USB link speed; it is retained for API compatibility. The board uses USB Full-Speed (FS) with a maximum packet size of 64 bytes. For hardware details, refer to Figure 793 (Page 2747) of the [STM32H747 Reference Manual] (OTG_FS) and the USB0 section in the [Arduino GIGA R1 Schematics].

On the host (PC), the OS driver reads from the CDC using URBs (USB Request Blocks). The URB read size is driver/OS dependent (on our Windows 11 test system it is 4096 bytes). A host read typically completes when either:

- The URB buffer fills, or
- The device sends a short packet (smaller than max packet size), or
- A driver-specific timeout occurs.

If the device continuously writes data in exact multiples of the USB max packet size (FS: 64 bytes), the driver may wait until an entire URB fills, increasing latency. To reduce latency, ensure each application-level chunk ends with a short packet.

In our EMG case, the short packet needs to be created manually; `Serial` doesn't offer a proper API to flush the URB. Prefer chunk sizes whose total byte count is not a multiple of the 64-byte max packet size, which naturally creates a short packet at the end of the URB. Alternatively, you could add small padding, so the final packet is short, and make the receiver ignore the pad. 

```c
static void transfer_buf(volatile uint16_t* data, uint16_t data_length) {
    uint8_t* ptr = (uint8_t*)data;
    Serial.write(ptr, data_length * sizeof(uint16_t));
}
```

Below is the table with measurements for different selected EMG chunks.

| EMG Chunk Size (samples) | EMG Chunk Size (bytes) | Measured Chunk Arrival Rate |
|:------|:------|:--------|
| 32    | 64    | 102 ms  |
| 64    | 128   | 103 ms  |
| 75    | 150   | 16 ms   |

The ultimate solutions include implementing a custom USB class or customizing the CDC driver to force short packets at frame boundaries. If you want to fix this, see the related [issue](https://github.com/ShiegeChan/SensEdu/issues/92).

## Signal Processing

EMG post-processing was made in MATLAB. You can find the main block diagram below. The main components of filtering contains of storing the data in a longer buffer, applying filtering, enveloping and making a decision based on the final processed data: either the button on the keyboartd is presed, hold or released.

[picture: block diagram]

### Problematic ADC Readings

First, let's discuss the incoming RAW data to MATLAB. There was noticed a weird behaviour with the first couple of samples at each measurement cycle. They always abnormally high and after 5-10 samples stabilized around expected values.

[picture: weired samples]

It is not certain what exactly causes this behaviour, most probably is high input capacitance to ADC due to using the electrodes and all this bio setup.

To fix it fast, script just removes the first 8 samples from each measurement cycle, using only stable ADC data, keep that in mind while calculating the sizes for next steps.

### The Buffer

After triggering the measurement cycle which lasts for $$d_{meas, ideal} = 40\mathrm{ms}$$, the incoming data is stored in a buffer that contains the whole **1 second** of these measurement cycles. Works like FIFO, the oldest measurement is out, the whole buffer shifts to the left and the freed up space is taken by the new one.

{: .NOTE}
The buffer size is calculated based on $$d_{meas, ideal}$$ which means that actual buffer contains data for a bit longer period than calculated.

Processing on this longer buffer helps multiple cycles of low-frequency components being captured and properly filtered out which improves filter's ability to attenuate noise and artifact and preservation of desired signal components.

A longer history allows low-pass filters (used in envelope detection) to smooth the rectified signal over a larger time frame, resulting in a more robust and stable envelope.

For example, a 5Hz low-pass filter requires at least 200ms of data for one full cycle. With a 1-second history, the envelope will be less sensitive to short-term fluctuations or noise.

Use a 1-second buffer for filtering and envelope detection, but process overlapping chunks (e.g., update every 40ms). This ensures that decisions are updated frequently without sacrificing the filtering accuracy of the longer window.

{: .NOTE}
There is a logic that doesn't start the plotting or decision making before the whole buffer is filled when you start the program.

### FIR Filter

Before filtering, the large DC offset is removed from the buffer (the signal sits around the ADC mid-scale, ~25000 counts). A linear-phase band-pass FIR (150 taps, 30–450 Hz) is then applied with `fir1`.

{: .NOTE}
DC removal must happen **before** the FIR, not rely on it. With 150 taps at $$f_s = 5\mathrm{kHz}$$ the filter transition is roughly $$f_s / \mathrm{TAPS} \approx 33\mathrm{Hz}$$ wide, so the 30 Hz lower edge cannot actually reject DC (the coefficients sum to ~0.2). If the offset is left in, the ~25000-count offset leaks ~5000 counts into the output and buries the EMG.

After filtering, the first `TAPS` (150) samples are discarded. This does two things at once: it removes the FIR start-up transient and compensates the constant $$\mathrm{TAPS}/2$$ group delay of the linear-phase filter, so the output stays time-aligned with the raw signal.

### Rectification

The band-passed signal is full-wave rectified (absolute value). Raw EMG is zero-mean, so rectification is what makes amplitude measures (mean, peak, area) meaningful and is the prerequisite for envelope extraction — all negative excursions are folded up about the baseline.

### Envelope

The rectified signal is low-pass filtered with a 2nd-order Butterworth at $$f_c = 10\mathrm{Hz}$$ to produce the **linear envelope**, a smooth estimate of muscle activation that the decision stage works on.

Because the system runs in real time, the envelope filter is applied **causally** (`filter`, not the zero-phase `filtfilt`, which needs the whole signal). A causal filter introduces a group delay, so its average delay below the cutoff is computed with `grpdelay` and trimmed from the front of the output, keeping the envelope aligned in time.

### Decision Block

Each channel drives **one game button** and is treated as a plain **gate, not a classifier**: a contraction presses the button DOWN, relaxing releases it UP. The game itself decides what a press means (e.g. in Dark Souls a short tap of B rolls, a held B sprints), so the controller never has to distinguish tap from hold — it just mirrors the muscle, pressing at the contraction onset (the latency-critical moment) and releasing after a short debounce.

{: .NOTE}
**Startup / calibration period.** A channel cannot fire until it has measured its rest floor, which needs the rolling buffer to fill plus a few seconds of resting data — so the controller is deliberately **unresponsive for roughly the first few seconds**. Allow about **15 seconds** to settle in: keep the muscles relaxed at first so each channel can fix its floor, then **contract each channel once** to teach it its press height. Until a channel has registered one clear press it uses a conservative default bar (`MIN_GAP` above the floor); a channel whose presses never reach that bar is pulled down to it by the self-recovery net over ~15 s.

#### Adaptive thresholds

A fixed threshold only ever fits one recording: muscle fatigue and electrode position make the envelope amplitude drift several-fold within and between sessions. The thresholds are therefore derived from two **decoupled** per-channel estimates, each measured only when it is valid. Decoupling them is what makes the gate independent of *how often* the muscle happened to be used recently — a plain "high percentile of the last N seconds" ceiling is **not**, because it silently tracks the duty cycle of contractions (a long quiet stretch collapses it and makes the gate hair-trigger; sparse presses under-estimate it).

* **floor** — the rest level. A low percentile (20th) of a rolling history that collects **only idle, sub-release samples**. Because contractions are excluded, a long sprint can never drag the floor up, while it still follows slow baseline drift (fatigue, sweat, electrode contact).
* **press height** ($$P$$) — the typical activation height *above* the floor. Learned from the **peaks of the contractions the gate actually finalizes**: each finished press nudges $$P$$ by a small EMA step after being clamped to $$0.5\text{–}2\times$$ the current $$P$$, so one unusually hard or weak press can never permanently re-scale the thresholds, and sparse presses keep the bar where the user's real presses are.

The working gap is $$g = \max\!\left(P,\ \mathrm{MIN\_GAP} / \mathrm{FRAC\_HIGH}\right)$$ — the second term is the cold-start / noise floor used before a press is learned. The thresholds are then

$$\mathrm{onset} = \mathrm{floor} + \mathrm{FRAC\_HIGH} \cdot g, \qquad \mathrm{release} = \mathrm{floor} + \mathrm{FRAC\_LOW} \cdot g$$

with FRAC_HIGH = 0.40 and FRAC_LOW = 0.20. Equivalently, normalising the envelope as $$n = (\mathrm{env} - \mathrm{floor}) / g$$ (≈0 at rest, ≈1 on a typical press), the gate fires at $$n \ge \mathrm{FRAC\_HIGH}$$ and releases at $$n \le \mathrm{FRAC\_LOW}$$.
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

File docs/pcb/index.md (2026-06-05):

---
title: PCB
layout: default
nav_order: 3
permalink: /pcb/
---

# PCB Design
{: .fs-8 .fw-500 .no_toc}
---

SensEdu focuses on the design and development of a Printed Circuit Board (PCB) tailored for the Arduino GIGA R1. The objective is to create a versatile and efficient platform capable of accommodating a wide range of ultrasound applications, ensuring optimal performance and ease of integration.
{: .fw-500}

- TOC
{:toc}
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

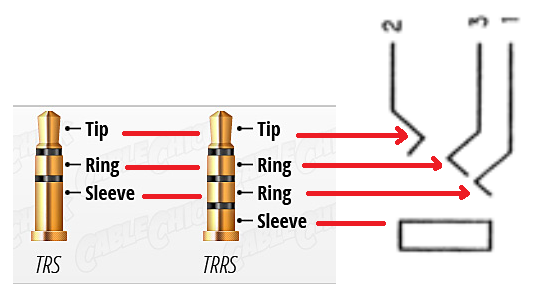
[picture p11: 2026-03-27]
docs/assets/images/MiniJackPinout.png

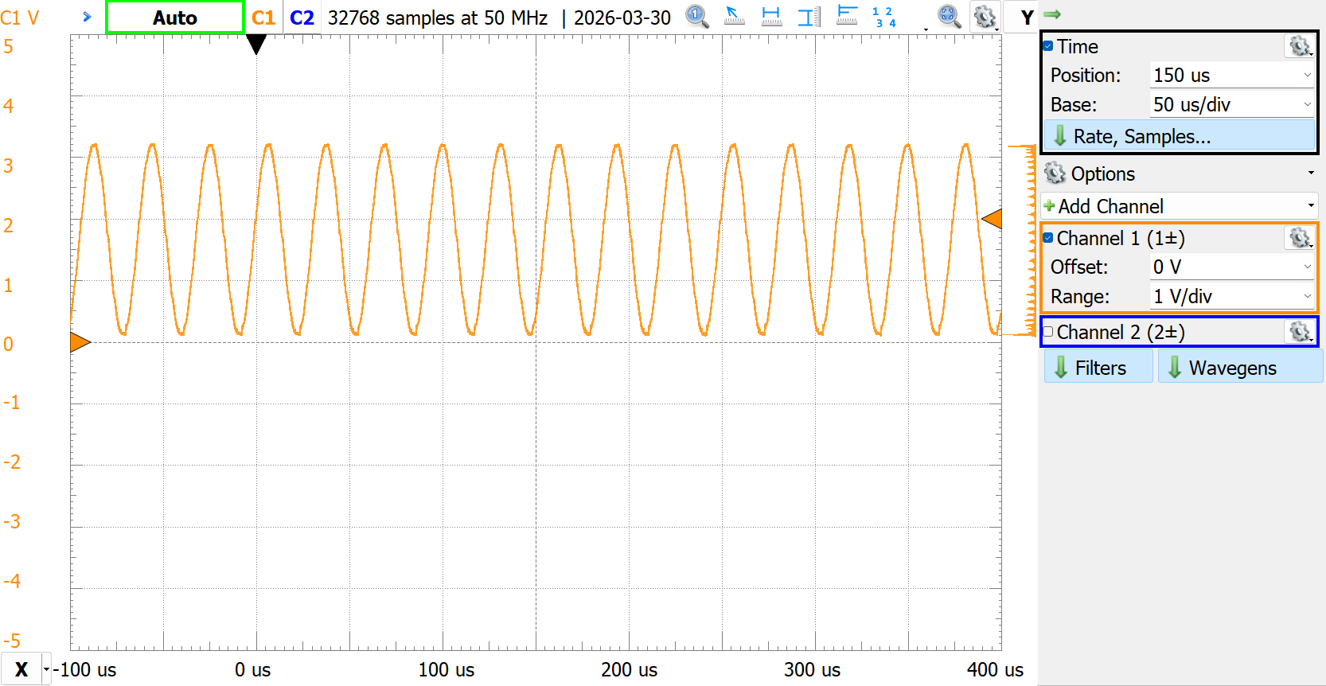
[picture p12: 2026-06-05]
docs/assets/images/dac_const_sine_example.png

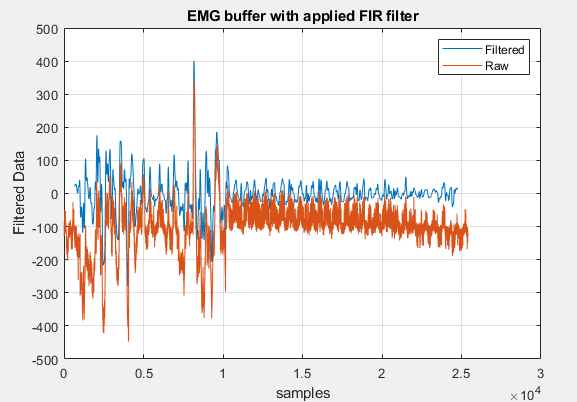
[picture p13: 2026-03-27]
projects/EMG-BioInputs/pics/raw_filtered_data.png

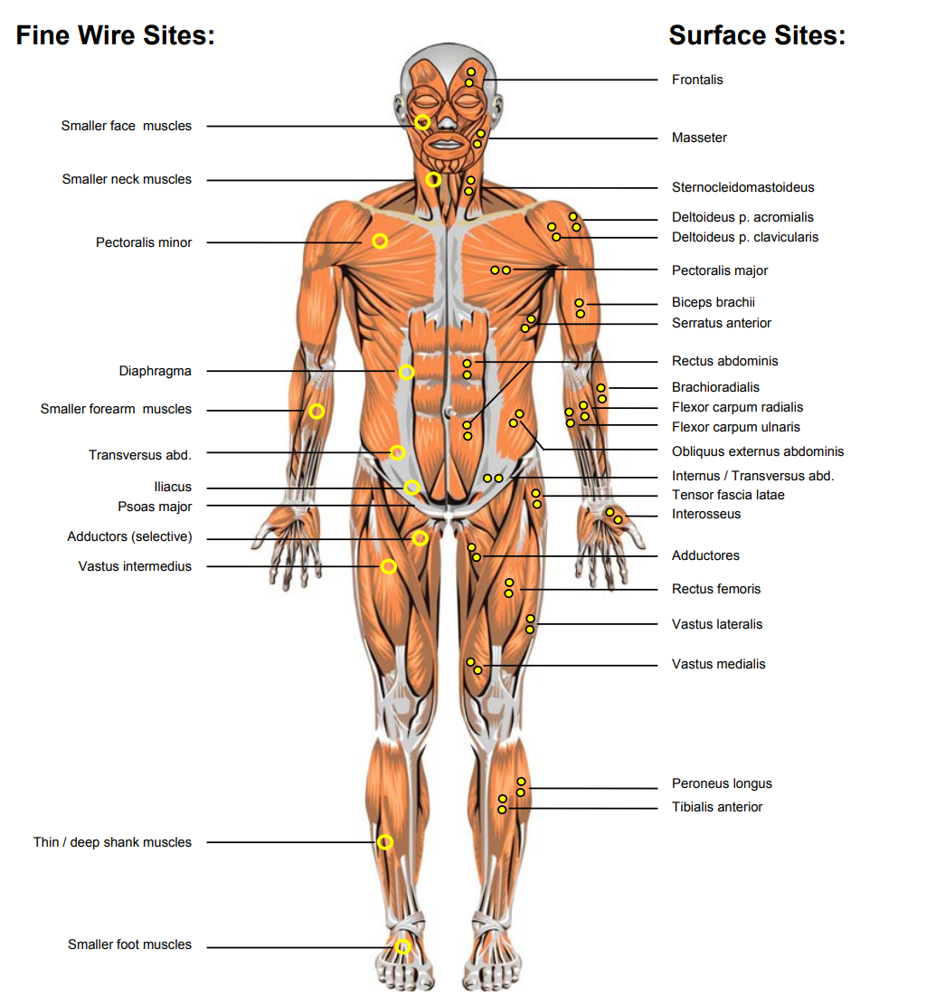
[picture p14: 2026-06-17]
docs/assets/images/electrode-placement.png

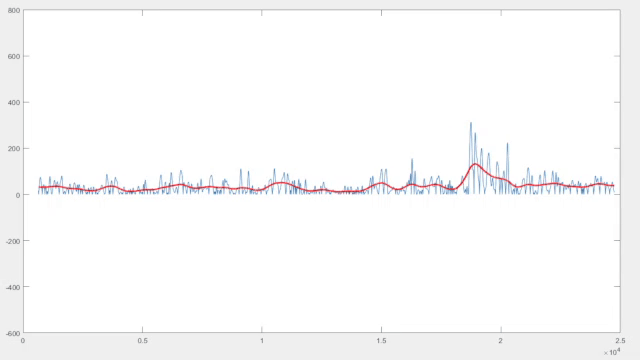
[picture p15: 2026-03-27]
projects/EMG-BioInputs/pics/ezgif-360ec1a0905344.gif

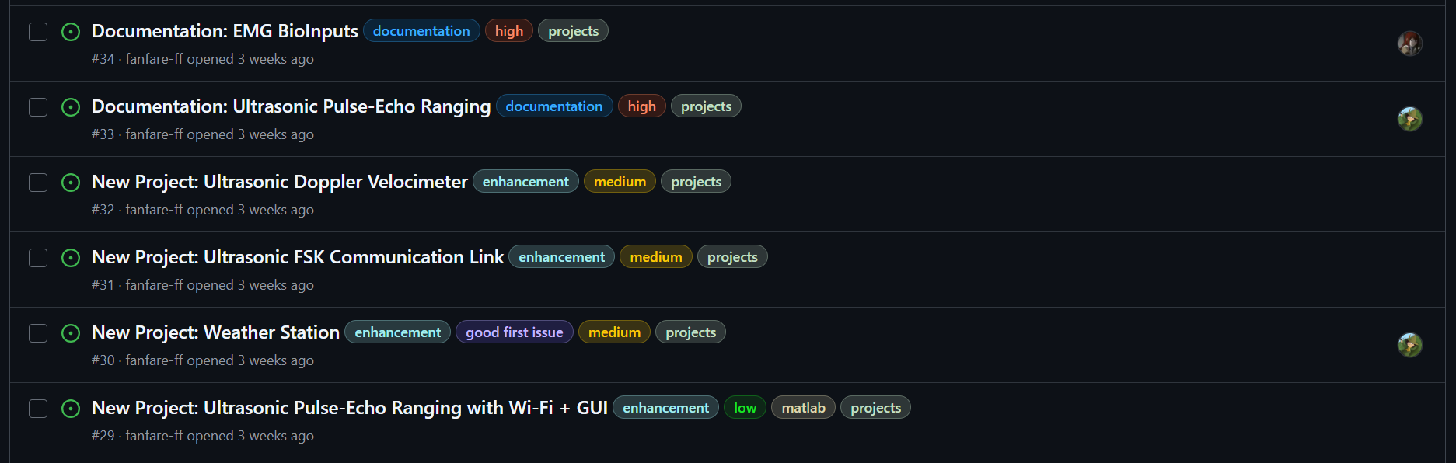
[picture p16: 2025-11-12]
docs/assets/images/roadmap.png

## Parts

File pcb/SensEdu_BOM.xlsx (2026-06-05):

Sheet: Sheet1
Reference | Value | Footprint | Qty | DNP | Price (per 10xQty) | Total Price | Part Number | Note | Link
C1,C2,C8,C9,C26,C27,C28,C29,C46,C47,C48,C49,C51,C54 | 1u | SensEdu:C_0603_1608Metric | 14 |  | €0.07 | €0.91 | GCJ188R71E105KA01D | 10%; X7R | https://www.mouser.de/ProductDetail/Murata-Electronics/GCJ188R71E105KA01D?qs=rnuWwpjhhVuRpUqK416FbQ%3D%3D
C3,C4 | 4.7u | SensEdu:C_0805_2012Metric | 2 |  | €0.13 | €0.27 | GCJ21BR71C475KA01L | 10%; X7R | https://www.mouser.de/ProductDetail/Murata-Electronics/GCJ21BR71C475KA01L?qs=AEetWsPH0ItHFBxw0%252BVnvA%3D%3D
C5,C7 | 2.2u | SensEdu:C_0805_2012Metric | 2 |  | €0.04 | €0.08 | CL21B225KAFNNNG | 10%; X7R | https://www.mouser.de/ProductDetail/Samsung-Electro-Mechanics/CL21B225KAFNNNG?qs=yOVawPpwOwljM4cRphaUPg%3D%3D
C6 | 470n | SensEdu:C_0603_1608Metric | 1 |  | €0.05 | €0.05 | GRM188R71A474JA61J | 5%; X7R | https://www.mouser.de/ProductDetail/Murata-Electronics/GRM188R71A474JA61J?qs=QzBtWTOodeWXuS9g9090Nw%3D%3D
C10,C11,C18,C19,C30,C31,C32,C33,C52,C53,C58,C59,C60 | 100n | SensEdu:C_0603_1608Metric | 13 |  | €0.01 | €0.07 | CL10B104JB8NNNC | 5%; X7R | https://www.mouser.de/ProductDetail/Samsung-Electro-Mechanics/CL10B104JB8NNNC?qs=349EhDEZ59oLEw5wc1qvGw%3D%3D
C12,C13,C20,C21,C34,C35,C36,C37 | 470p | SensEdu:C_0603_1608Metric | 8 |  | €0.08 | €0.66 | GCM1885C2A471FA16D | 1%; C0G | https://www.mouser.de/ProductDetail/Murata-Electronics/GCM1885C2A471FA16D?qs=QzBtWTOodeWgqjEsX2PjAg%3D%3D
C14,C15,C16,C17,C22,C23,C24,C25,C38,C39,C40,C41,C42,C43,C44,C45 | 100p | SensEdu:C_0603_1608Metric | 16 |  | €0.04 | €0.66 | GQM1875C2E101FB12D | 2%; C0G | https://www.mouser.de/ProductDetail/Murata-Electronics/GQM1875C2E101FB12D?qs=5aG0NVq1C4xaBfxwcpvDIQ%3D%3D
C50,C57 | 1n | SensEdu:C_0603_1608Metric | 2 |  | €0.05 | €0.10 | GCM1885C2A102FA16D | 1%; C0G | https://mou.sr/3Q4kneA
C55,C56 | DNI | SensEdu:C_0603_1608Metric | 2 | DNP |  | €0.00
D1 | LED | SensEdu:LED_0805_2012Metric | 1 |  | €0.13 | €0.13 | 598-8170-107F |  | https://www.mouser.de/ProductDetail/Dialight/598-8170-107F?qs=7JStj%2FjQ2SEAJGswzKZPeg%3D%3D
J1,J3,J4,J5,J6 | 1x8 Housing | SensEdu:PinSocket_1x08_P2.54mm_Vertical | 5 |  | €1.51 | €7.55 | SSQ-108-03-G-S |  | https://www.mouser.de/ProductDetail/Samtec/SSQ-108-03-G-S?qs=92ilVni64gxESeLoQPf0Dw%3D%3D
J2 | 1x10 Housing | SensEdu:PinSocket_1x10_P2.54mm_Vertical | 1 |  | €2.28 | €2.28 | SSQ-110-03-G-S |  | https://www.mouser.de/ProductDetail/Samtec/SSQ-110-03-G-S?qs=0u6pJ%2FESxi2TyhdgZpByhg%3D%3D
J7 | 2x18 Housing | SensEdu:PinSocket_2x18_P2.54mm_Vertical | 1 | DNP |  | €0.00
J8,J9,J10,J11 | 1x4 Housing | SensEdu:PinSocket_1x04_P2.54mm_Vertical | 4 |  | €1.16 | €4.64 | SSW-104-01-G-S |  | https://www.mouser.de/ProductDetail/Samtec/SSW-104-01-G-S?qs=92ilVni64gwX57oPv1Qypw%3D%3D
MK1,MK2,MK3,MK4 | IM73A135V01XTSA1 | SensEdu:MIC_IM73A135V01XTSA1 | 4 |  | €1.41 | €5.64 | IM73A135V01XTSA1 |  | https://mou.sr/4aXaWrH
R1,R4 | 130k | SensEdu:R_0603_1608Metric | 2 |  | €0.04 | €0.08 | ERA-3AED134V | 0.5%; 100mW; 25ppm | https://www.mouser.de/ProductDetail/Panasonic/ERA-3AED134V
R2,R3 | 75k | SensEdu:R_0603_1608Metric | 2 |  | €0.18 | €0.35 | ERA-3APB753V | 0.1%; 100mW; 15ppm | https://www.mouser.de/ProductDetail/Panasonic/ERA-3APB753V?qs=sGAEpiMZZMtlubZbdhIBIJiMSTY83nT4BTj01APdFCo%3D
R5 | 47 | SensEdu:R_0603_1608Metric | 1 |  | €0.05 | €0.05 | ERA-3AEB470V | 0.1%; 100mW; 25ppm | https://www.mouser.de/ProductDetail/Panasonic/ERA-3AEB470V
R6,R7,R8,R9,R10,R11,R12,R13,R18,R19,R20,R21,R22,R23,R24,R25 | 3.9k | SensEdu:R_0603_1608Metric | 16 |  | €0.05 | €0.74 | ERA-3AEB392V | 0.1%; 100mW; 25ppm | https://www.mouser.de/ProductDetail/Panasonic/ERA-3AEB392V?qs=sGAEpiMZZMtlubZbdhIBIPpxc3aYtFQfw6EPxhWaWEc%3D
R14,R15,R16,R17,R26,R27,R28,R29 | 1k | SensEdu:R_0603_1608Metric | 8 |  | €0.05 | €0.37 | ERA-3AEB102V | 0.1%; 100mW; 25ppm | https://www.mouser.de/ProductDetail/Panasonic/ERA-3AEB102V
R30,R39 | 43k | SensEdu:R_0603_1608Metric | 2 |  | €0.05 | €0.09 | ERA-3AEB433V | 0.1%; 100mW; 25ppm | https://mou.sr/3PpuldV
R31,R35 | 100 | SensEdu:R_0603_1608Metric | 2 |  | €0.07 | €0.13 | ERA-3AED101V | 0.5%; 100mW; 25ppm | https://mou.sr/3xkErUr
R32,R33,R36,R38 | 22k | SensEdu:R_0603_1608Metric | 4 |  | €0.06 | €0.25 | ERJ-PB3B2202V | 0.1%; 200mW; 50ppm | https://www.mouser.de/ProductDetail/Panasonic/ERJ-PB3B2202V?qs=RYIBGgAklzKQbmWsiWLONA%3D%3D
R34,R37 | DNI | SensEdu:R_0603_1608Metric | 2 | DNP |  | €0.00
R40,R41,R42,R43 | 10k | SensEdu:R_0603_1608Metric | 4 |  | €0.06 | €0.23 | ERJ-PB3B1002V | 0.1%; 200mW; 50ppm | https://www.mouser.de/ProductDetail/Panasonic/ERJ-PB3B1002V?qs=RYIBGgAklzLBKZE0dH9NHQ%3D%3D
TP1,TP2,TP5,TP6 | Power TP | SensEdu:TestPoint_THTPad_D2.0mm_Drill1.0mm | 4 |  | €0.29 | €1.15 | 5000 |  | https://www.mouser.de/ProductDetail/Keystone-Electronics/5000?qs=q0tsjPZWdm%252B9SiiTAbEwUw%3D%3D
TP3,TP4 | GND TP | SensEdu:5018 | 2 |  | €0.28 | €0.56 | 5018 |  | https://mou.sr/40UKP08
TP7,TP8,TP9,TP10 | Signal TP | SensEdu:TestPoint_THTPad_D2.0mm_Drill1.0mm | 4 |  | €0.19 | €0.76 | 5001 |  | https://www.mouser.de/ProductDetail/Keystone-Electronics/5001?qs=q0tsjPZWdm%2FW0vdr%2FwowKg%3D%3D
TX1,TX2 | 328ST16M | SensEdu:328ST16M_Speaker | 2 |  | €6.50 | €13.00 | 328ST16M |  | https://www.mouser.de/ProductDetail/Pro-Wave-Electronics/328ST16M?qs=gTYE2QTfZfQM3XaGKNA7nw%3D%3D
U1 | LDLN025M25R | SensEdu:SOT95P280X145-5N | 1 |  | €0.39 | €0.39 | LDLN025M25R |  | https://www.mouser.de/ProductDetail/STMicroelectronics/LDLN025M25R?qs=5aG0NVq1C4wSHhiEnEzM%2Fg%3D%3D
U2 | LM27762DSST | SensEdu:IC_LM27762DSST | 1 |  | €1.54 | €1.54 | LM27762DSST |  | https://www.mouser.de/ProductDetail/Texas-Instruments/LM27762DSST?qs=vcbl%252BK4rRlcgKmrBHASI8g%3D%3D
U3 | TS3312AQPR | SensEdu:TS3312AQPR | 1 |  | €0.76 | €0.76 | TS3312AQPR |  | https://www.mouser.de/ProductDetail/STMicroelectronics/TS3312AQPR?qs=1mbolxNpo8d3EIZUP0Dh4w%3D%3D
U4,U5,U6,U7 | AD8426ACPZ-R7 | SensEdu:QFN65P400X400X100-16N | 4 |  | €5.41 | €21.64 | AD8426ACPZ-R7 |  | https://www.mouser.de/ProductDetail/Analog-Devices/AD8426ACPZ-R7?qs=%2FtpEQrCGXCy0%2F9Zrxy%252BnYw%3D%3D
U8 | ADA4511-2ARMZ | SensEdu:SOP65P490X110-8N | 1 |  | €2.43 | €2.43 | ADA4511-2ARMZ |  | https://www.mouser.de/ProductDetail/Analog-Devices/ADA4511-2ARMZ?qs=yc9RBI4tIAK9W%2FurDZsowQ%3D%3D
U9 | DPS368XTSA1 | SensEdu:DPS368XTSA1 | 1 |  | €2.27 | €2.27 | DPS368XTSA1 |  | https://www.mouser.de/ProductDetail/Infineon-Technologies/DPS368XTSA1?qs=l7cgNqFNU1issZx9oeCNag%3D%3D
U10 | SHT40-AD1F-R2 | SensEdu:SHT40AD1FR2 | 1 |  | €1.56 | €1.56 | SHT40-AD1F-R2 |  | https://mou.sr/3NYpzUa
 |  |  |  |  |  | €71.39

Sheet: SensEdu
Reference,"Value","Footprint","Qty","DNP"
C1,C2,C8,C9,C26,C27,C28,C29,C46,C47,C48,C49,C51,C54,"1u","SensEdu:C_0603_1608Metric","14",""
C3,C4,"4.7u","SensEdu:C_0805_2012Metric","2",""
C5,C7,"2.2u","SensEdu:C_0805_2012Metric","2",""
C6,"470n","SensEdu:C_0603_1608Metric","1",""
C10,C11,C18,C19,C30,C31,C32,C33,C52,C53,C58,C59,C60,"100n","SensEdu:C_0603_1608Metric","13",""
C12,C13,C20,C21,C34,C35,C36,C37,"470p","SensEdu:C_0603_1608Metric","8",""
C14,C15,C16,C17,C22,C23,C24,C25,C38,C39,C40,C41,C42,C43,C44,C45,"100p","SensEdu:C_0603_1608Metric","16",""
C50,C57,"1n","SensEdu:C_0603_1608Metric","2",""
C55,C56,R34,R37,"DNI","SensEdu:C_0603_1608Metric,SensEdu:R_0603_1608Metric","4","DNP"
D1,"LED","SensEdu:LED_0805_2012Metric","1",""
J1,"Power","SensEdu:PinSocket_1x08_P2.54mm_Vertical","1",""
J2,J4,"PWM","SensEdu:PinSocket_1x08_P2.54mm_Vertical,SensEdu:PinSocket_1x10_P2.54mm_Vertical","2",""
J3,J5,"Analog","SensEdu:PinSocket_1x08_P2.54mm_Vertical","2",""
J6,"Communication","SensEdu:PinSocket_1x08_P2.54mm_Vertical","1",""
J7,"Digital","SensEdu:PinSocket_2x18_P2.54mm_Vertical","1","DNP"
J8,J9,J10,J11,"Conn_01x04_Pin","SensEdu:PinSocket_1x04_P2.54mm_Vertical","4",""
MK1,MK2,MK3,MK4,"IM73A135V01XTSA1","SensEdu:MIC_IM73A135V01XTSA1","4",""
R1,R4,"130k","SensEdu:R_0603_1608Metric","2",""
R2,R3,"75k","SensEdu:R_0603_1608Metric","2",""
R5,"47","SensEdu:R_0603_1608Metric","1",""
R6,R7,R8,R9,R10,R11,R12,R13,R18,R19,R20,R21,R22,R23,R24,R25,"3.9k","SensEdu:R_0603_1608Metric","16",""
R14,R15,R16,R17,R26,R27,R28,R29,"1k","SensEdu:R_0603_1608Metric","8",""
R30,R39,"43k","SensEdu:R_0603_1608Metric","2",""
R31,R35,"100","SensEdu:R_0603_1608Metric","2",""
R32,R33,R36,R38,"22k","SensEdu:R_0603_1608Metric","4",""
R40,R41,R42,R43,"10k","SensEdu:R_0603_1608Metric","4",""
TP1,"+2.5V","SensEdu:TestPoint_THTPad_D2.0mm_Drill1.0mm","1",""
TP2,"+3.3V","SensEdu:TestPoint_THTPad_D2.0mm_Drill1.0mm","1",""
TP3,TP4,"5018","SensEdu:5018","2",""
TP5,"+1.25V","SensEdu:TestPoint_THTPad_D2.0mm_Drill1.0mm","1",""
TP6,"-3.3V","SensEdu:TestPoint_THTPad_D2.0mm_Drill1.0mm","1",""
TP7,"DAC1","SensEdu:TestPoint_THTPad_D2.0mm_Drill1.0mm","1",""
TP8,"TX1","SensEdu:TestPoint_THTPad_D2.0mm_Drill1.0mm","1",""
TP9,"TX2","SensEdu:TestPoint_THTPad_D2.0mm_Drill1.0mm","1",""
TP10,"DAC0","SensEdu:TestPoint_THTPad_D2.0mm_Drill1.0mm","1",""
TX1,TX2,"328ST16M","SensEdu:328ST16M_Speaker","2",""
U1,"LDLN025M25R","SensEdu:SOT95P280X145-5N","1",""
U2,"LM27762DSST","SensEdu:IC_LM27762DSST","1",""
U3,"TS3312AQPR","SensEdu:TS3312AQPR","1",""
U4,U5,U6,U7,"AD8426ACPZ-R7","SensEdu:QFN65P400X400X100-16N","4",""
U8,"ADA4511-2ARMZ","SensEdu:SOP65P490X110-8N","1",""
U9,"DPS368XTSA1","SensEdu:DPS368XTSA1","1",""
U10,"SHT40-AD1F-R2","SensEdu:SHT40AD1FR2","1",""

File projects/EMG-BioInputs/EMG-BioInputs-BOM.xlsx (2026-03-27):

Name | Product Code | Quantity | 1x Price | Total | Link | Notes:
SENSOR CABLE - ELECTRODE PADS | 12970 | 12 | €8.44 | €101.28 | https://www.digikey.at/de/products/detail/sparkfun-electronics/12970/6833933
CONN HEADER R/A 4POS 2.54MM | 0901210124 | 25 | €0.51 | €12.83 | https://www.digikey.at/en/products/detail/molex/0901210124/760813 | socket for reference: | https://www.farnell.com/datasheets/2925583.pdf?_gl=1*4kzof5*_gcl_au*MjAyMzgyNzc1OC4xNzQ2NzAzOTEy
3.5mm F PCB Headphone Jack | 35RASMT2BHNTRX | 25 | €1.52 | €37.91 | https://www.digikey.at/en/products/detail/switchcraft-inc/35RASMT2BHNTRX/1291178 | clear length info: | https://eu.mouser.com/ProductDetail/Molex/90121-0124?qs=PvP5v7EimskrWnL4DJlIPg%3D%3D
Electrodes Type 1 | 3M Red Dot 2660-5 | 8 | €4.90 | €39.20 | https://www.kardiodepot.at/s/46503_319169_-3m-red-dot-2660-5-holter-elektroden-rontgentransluzent
Electrodes Type 2 | 3M Red Dot 2560 | 2 | €12.60 | €25.20 | https://www.kardiodepot.at/s/46503_319164_-3m-red-dot-2560-holter-elektroden
Electrodes Type 3 | Clinical L55H-Elektroden | 2 | €9.20 | €18.40 | https://www.kardiodepot.at/s/46588_367004_clinical-l55h-elektroden-fur-holter
 |  |  |  | €234.81

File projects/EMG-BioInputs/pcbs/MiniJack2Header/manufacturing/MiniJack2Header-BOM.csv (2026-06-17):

Id | Designator | Footprint | Quantity | Designation | Supplier and ref
1 | J1 | 35RASMT2BHNTRX | 1 | 35RASMT2BHNTRX
2 | J2 | CONN04_901210124_MOL | 1 | 901210124

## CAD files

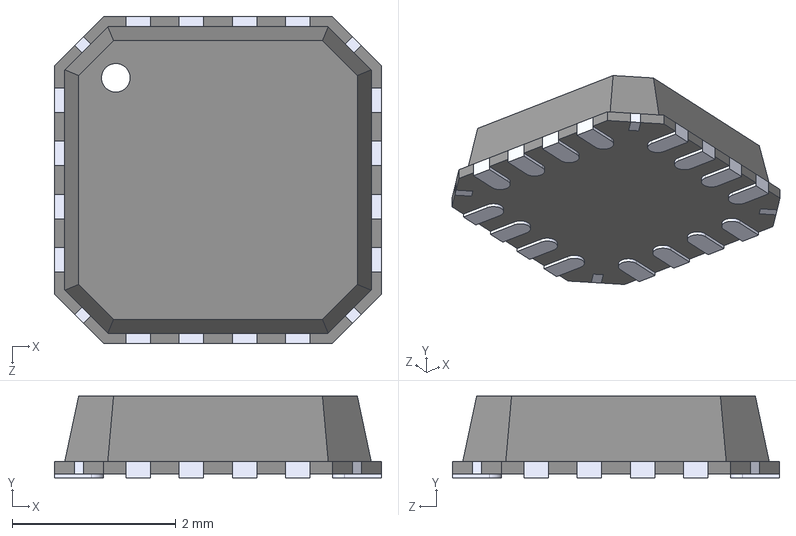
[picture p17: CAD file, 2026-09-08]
projects/Ultrasonic_3D_Tracking/pcbs/sensedu-extended-kicad/AD8426/AD8426ACPZ-R7.step
4.00 x 1.00 x 4.00 mm

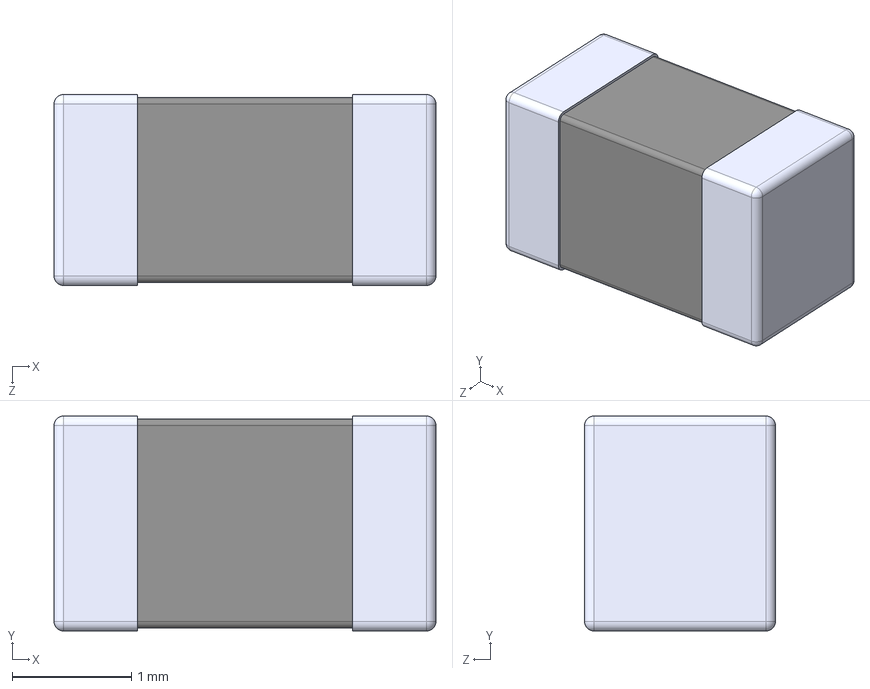
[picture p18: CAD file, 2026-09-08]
projects/Ultrasonic_3D_Tracking/pcbs/sensedu-extended-kicad/BLM31KN471SH1L/BLM31KN471SH1L.step
3.20 x 1.80 x 1.60 mm

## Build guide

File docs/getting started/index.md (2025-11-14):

---
title: Getting Started
layout: default
nav_order: 2
permalink: /getting-started/
---

# Getting Started
{: .fs-8 .fw-500 .no_toc}
---

Follow these steps to begin developing your projects with SensEdu.
{: .fw-500}

{: .NOTE}
*If you prefer video tutorials, we have an [installation guide] on YouTube (not yet).*

**Step 1**{: .text-green-200} : Connect SensEdu Shield to the Arduino GIGA R1. **By default, the power and speakers are disabled.** To enable them, place a small [2-pin jumper](https://mou.sr/41uQmLm) onto headers **J18**, **J17**, and **J8**, according to the desired settings. The standard configuration is shown in the figure below (more details in [PCB section]({% link pcb/index.md%}#key-headersjumpers))


{: .text-center}

**Step 2**{: .text-green-200} : Download and Install [Arduino IDE]

**Step 3**{: .text-green-200} : Open the *Boards Manager* tab, search for `giga` and install the latest version of *Arduino Mbed OS Giga Boards* package


{: .text-center}

**Step 4**{: .text-green-200} : Download the latest [SensEdu release]


{: .text-center}

**Step 5**{: .text-green-200} : Unzip downloaded files to a preferred location on your system

<video muted controls playsinline>
    <source src="{{site.baseurl}}/assets/videos/install_unzip.mp4" type="video/mp4">
    Video is broken.
</video>

**Step 6**{: .text-green-200} : Move extracted contents of `library` folder to the Arduino folder `My Documents\Arduino\libraries\`

<video muted controls playsinline>
    <source src="{{site.baseurl}}/assets/videos/install_libs.mp4" type="video/mp4">
    Video is broken.
</video>

**Step 7**{: .text-green-200} : Navigate to `File → Examples → SensEdu` and select `Blink_Delay` example

**Step 8**{: .text-green-200} : Select `Arduino Giga R1` board and corresponding COM port

**Step 9**{: .text-green-200} : Click **Upload** to compile and upload the sketch to your board. If the built-in LED starts blinking, the setup was successful!


{: .text-center}


{: .text-center}

## Post-Setup

Now that your setup is complete, you can start developing your projects with SensEdu! Here are some next steps to get started:
* Explore the [Library]({% link library/index.md %}) wiki section for detailed examples of each peripheral
* Check out sample projects in `projects\` folder, and respective [Projects]({% link projects/index.md %}) section
* For troubleshooting or guidance, visit the [Help]({% link help/index.md %}) section

{: .NOTE}
If you are interested in contributing to SensEdu, visit the [Contributing]({% link contributing/index.md %}) page and join our community!

[Arduino IDE]: https://support.arduino.cc/hc/en-us/articles/360019833020-Download-and-install-Arduino-IDE
[SensEdu release]: https://github.com/ShiegeChan/SensEdu/releases/
[installation guide]: https://www.youtube.com/

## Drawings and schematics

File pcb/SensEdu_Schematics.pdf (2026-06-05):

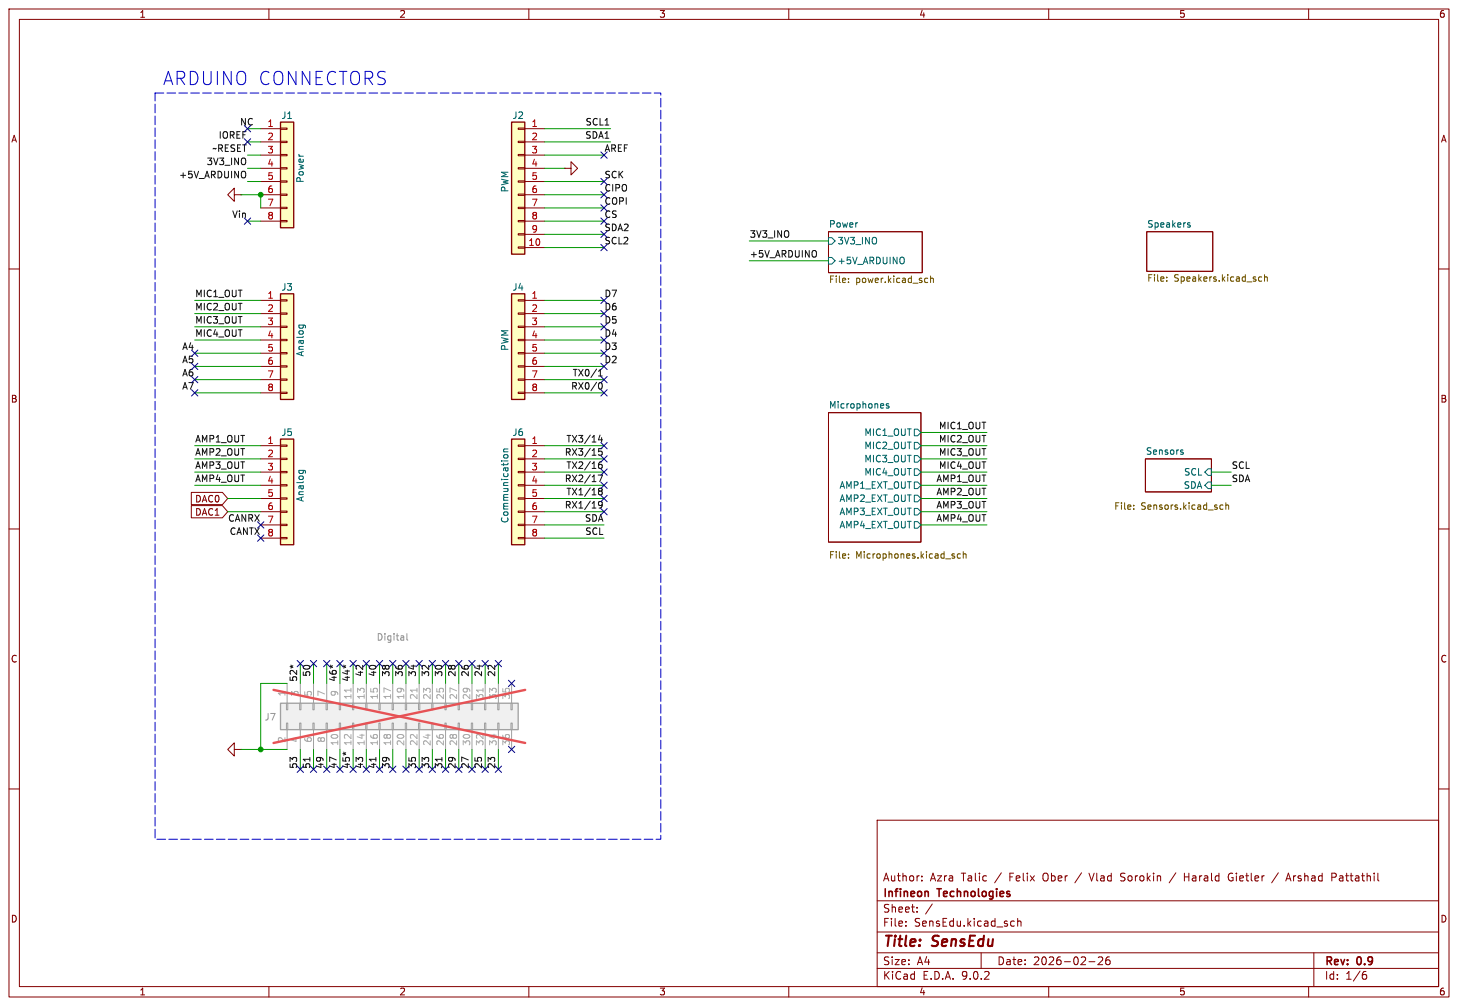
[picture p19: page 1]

CSCOPI SDA1SCL2 AREF SCL1SDA2 ARDUINO CONNECTORS

Speakers File: Speakers.kicad_sch SDA

SCL Sensors File: Sensors.kicad_sch

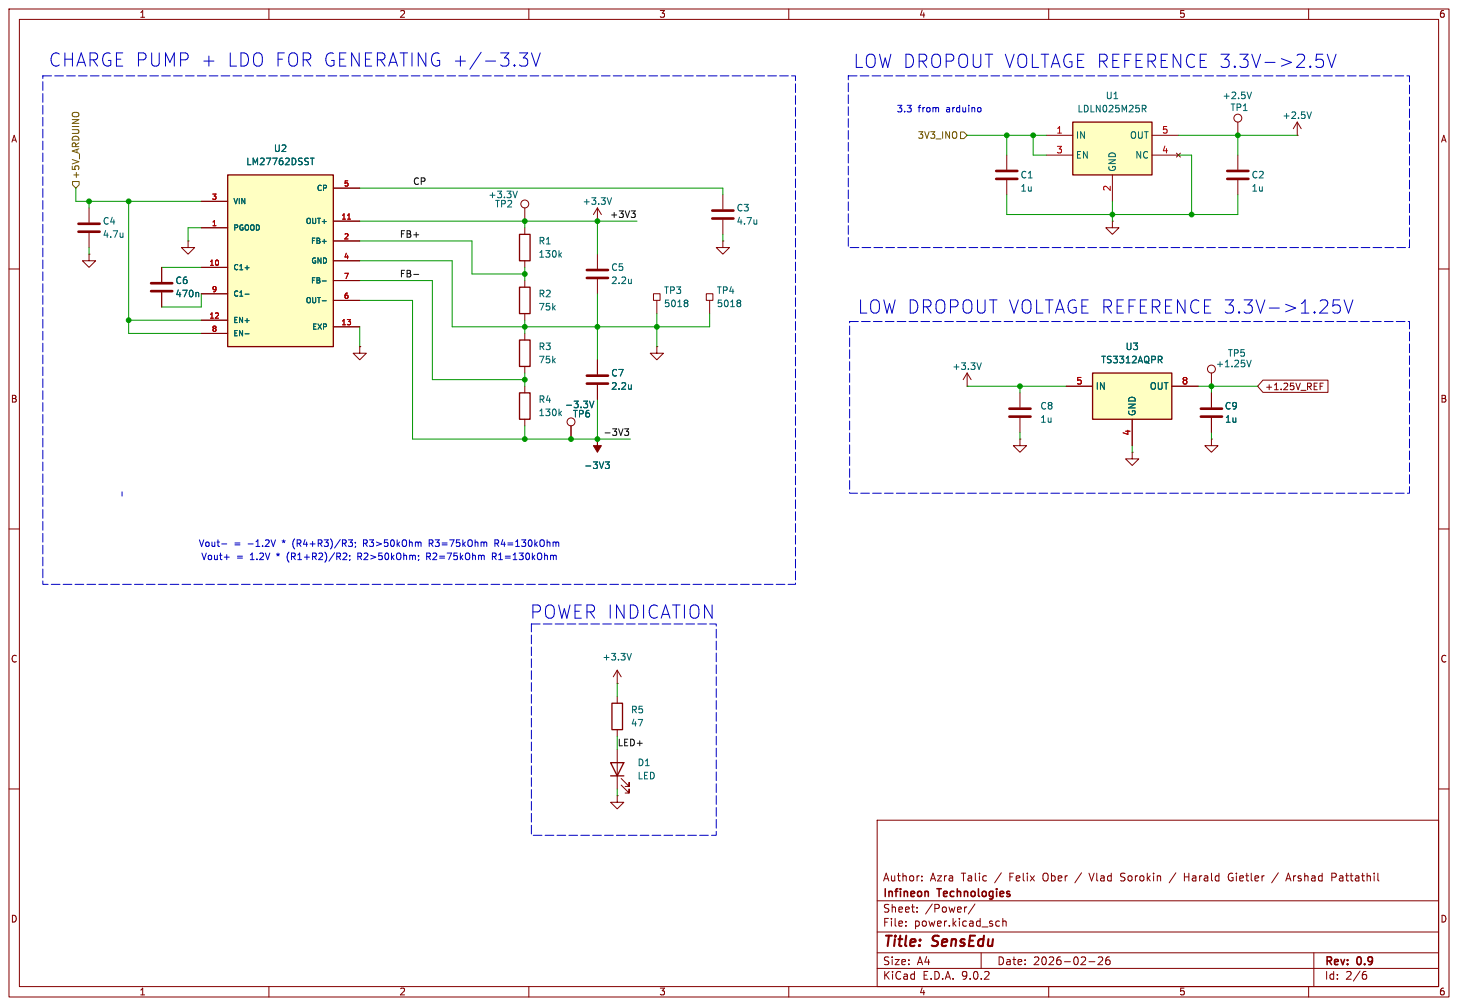
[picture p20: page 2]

3.3 from arduino CHARGE PUMP + LDO FOR GENERATING +/-3.3V

File: power.kicad_sch Sheet: /Power/
Id: 2/6 Title: SensEdu

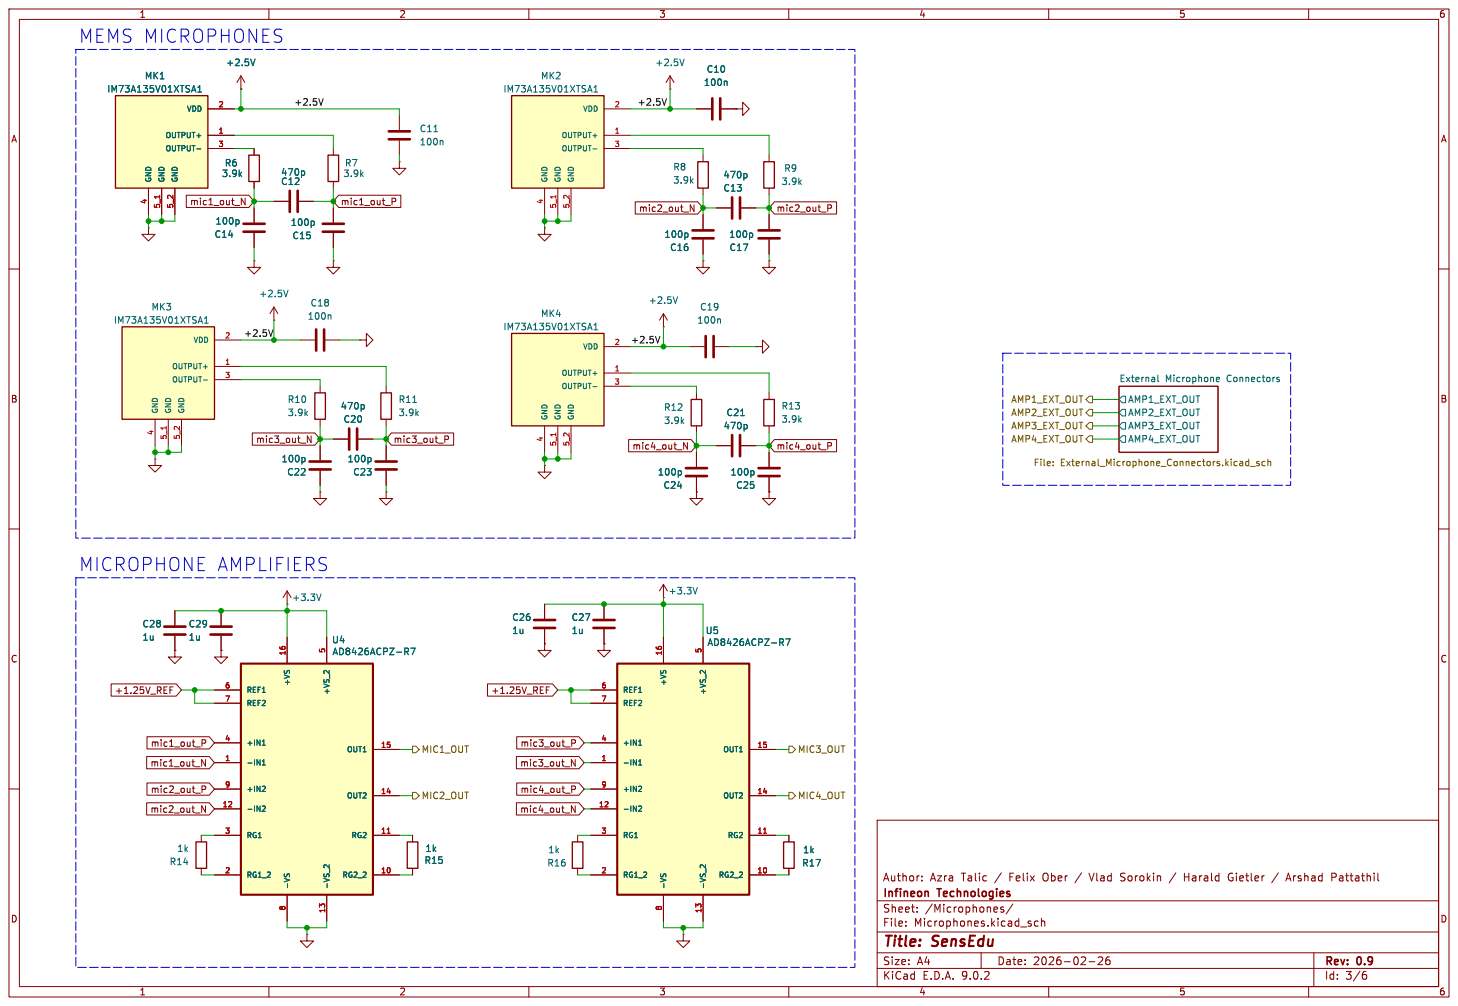
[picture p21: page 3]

4 GND 5_1 GND 5_2 VDD 2 OUTPUT+ 1 OUTPUT- 3 MK1

4 GND 5_1 GND 5_2 VDD 2 OUTPUT+ 1 OUTPUT- 3 MK2

4 GND 5_1 GND 5_2 VDD 2 OUTPUT+ 1 OUTPUT- 3C14

4 GND 5_1 GND 5_2 VDD 2 OUTPUT+ 1 OUTPUT- 3 MK3
100n GND

4 GND 5_1 GND 5_2 VDD 2 OUTPUT+ 1 OUTPUT- 3 MK4

File: Microphones.kicad_sch Sheet: /Microphones/
Id: 3/6 Title: SensEdu

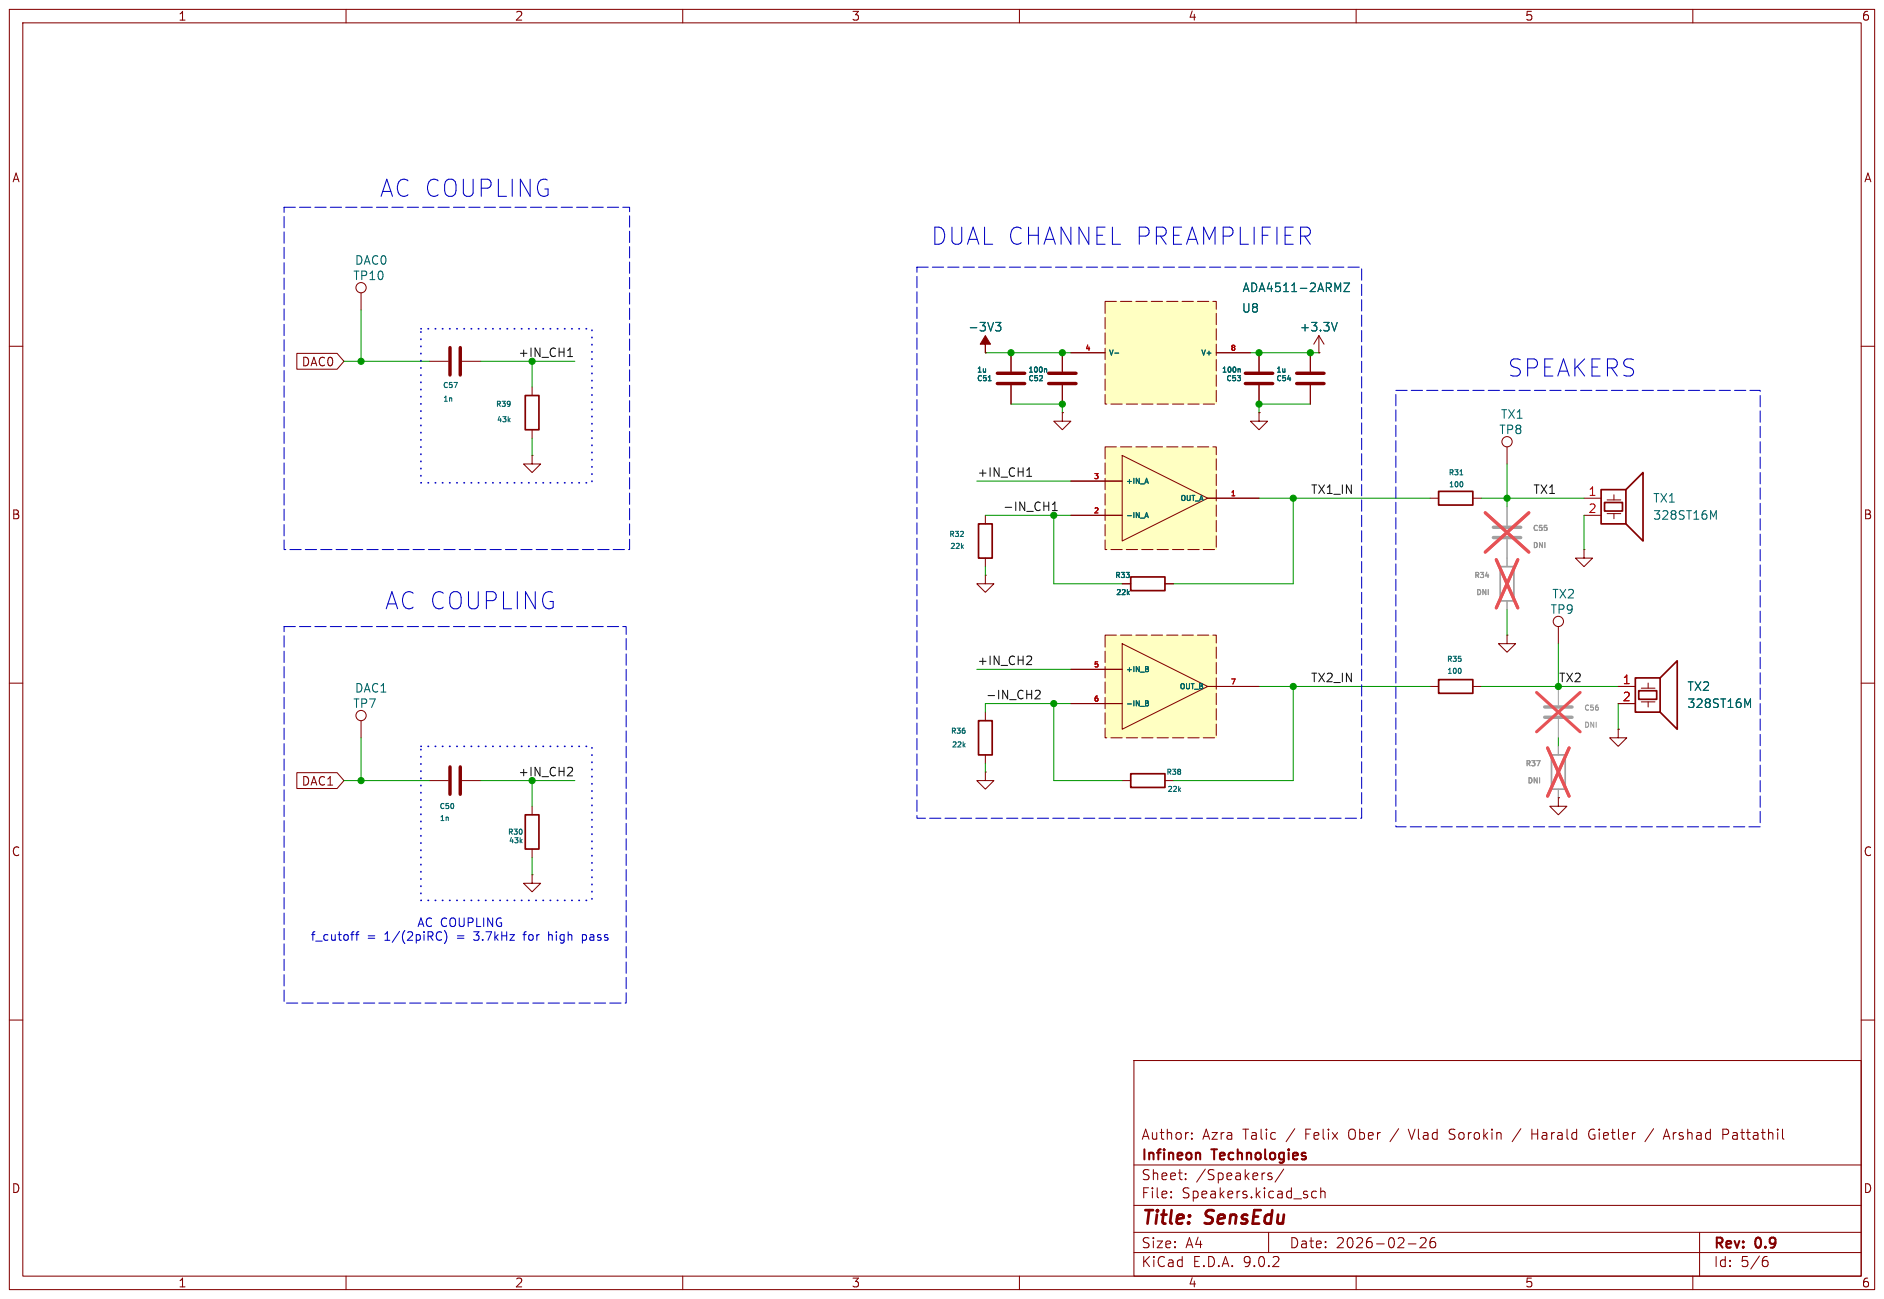
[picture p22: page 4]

File: Speakers.kicad_sch Sheet: /Speakers/
Id: 5/6 Title: SensEdu

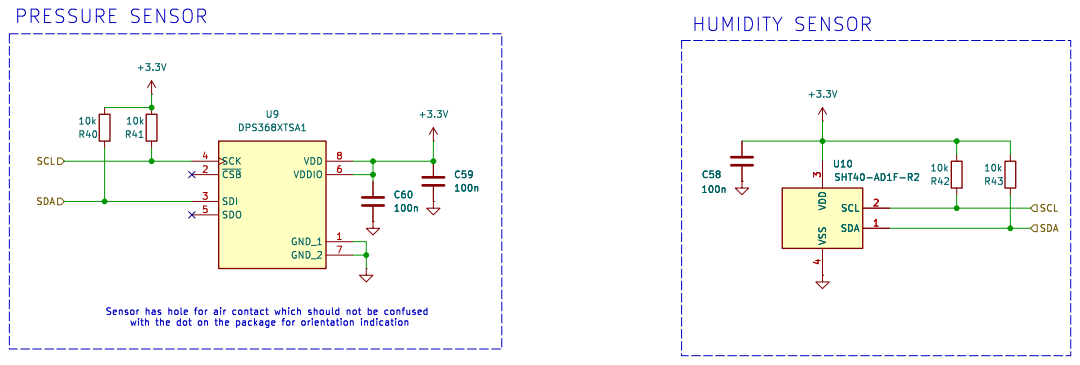
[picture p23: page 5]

File: Sensors.kicad_sch Sheet: /Sensors/
Id: 6/6 Title: SensEdu

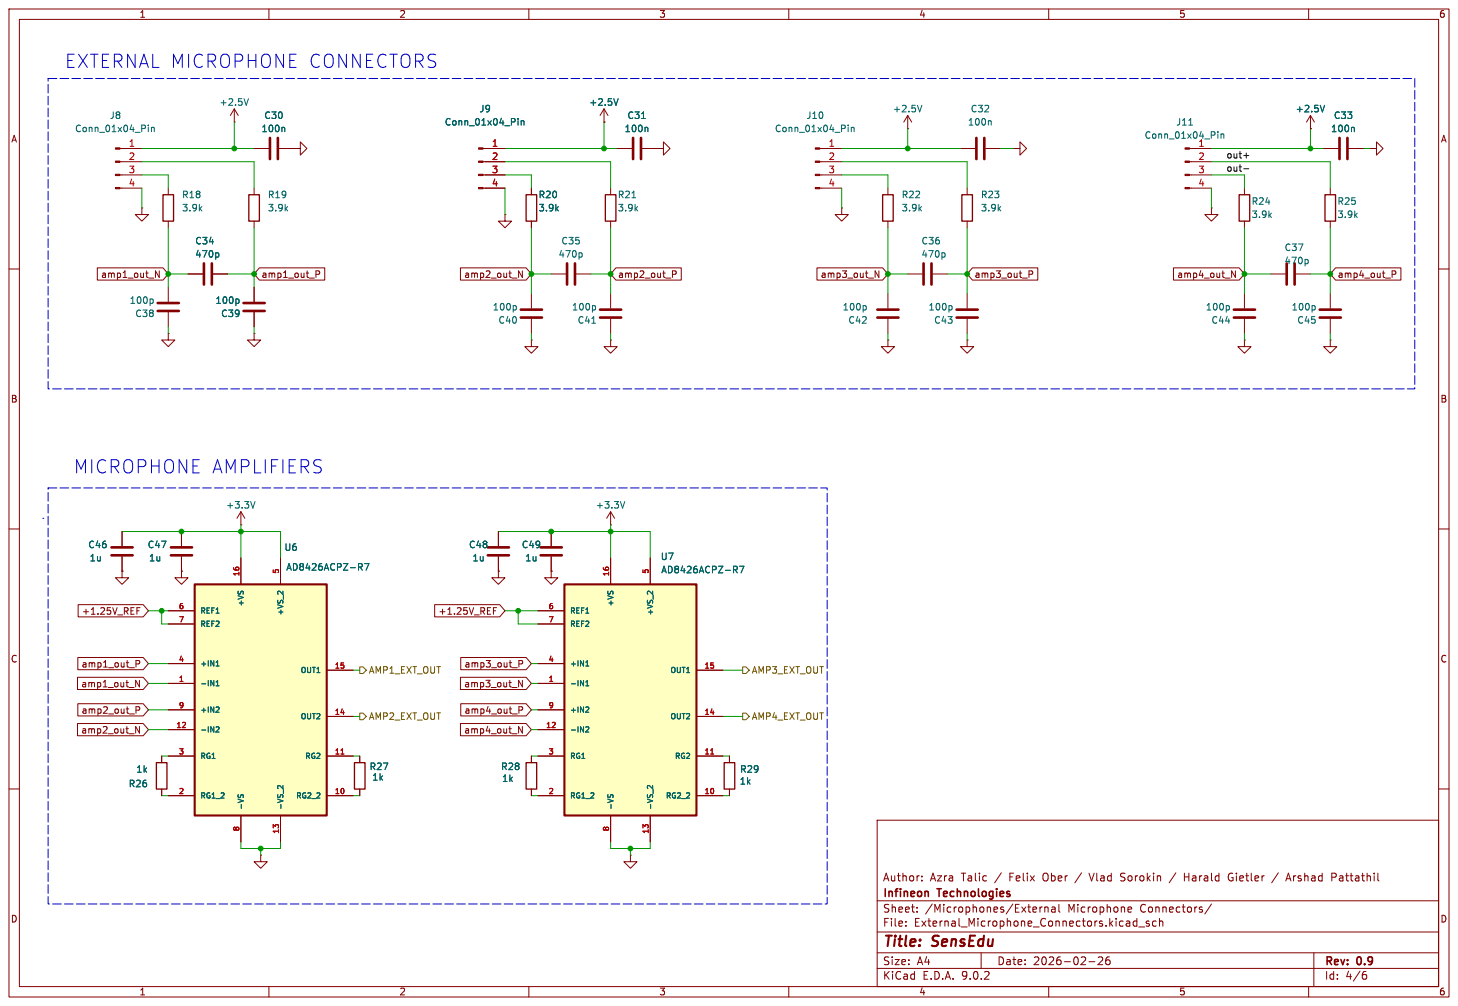
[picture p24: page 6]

EXTERNAL MICROPHONE CONNECTORS
out- out+ MICROPHONE AMPLIFIERS

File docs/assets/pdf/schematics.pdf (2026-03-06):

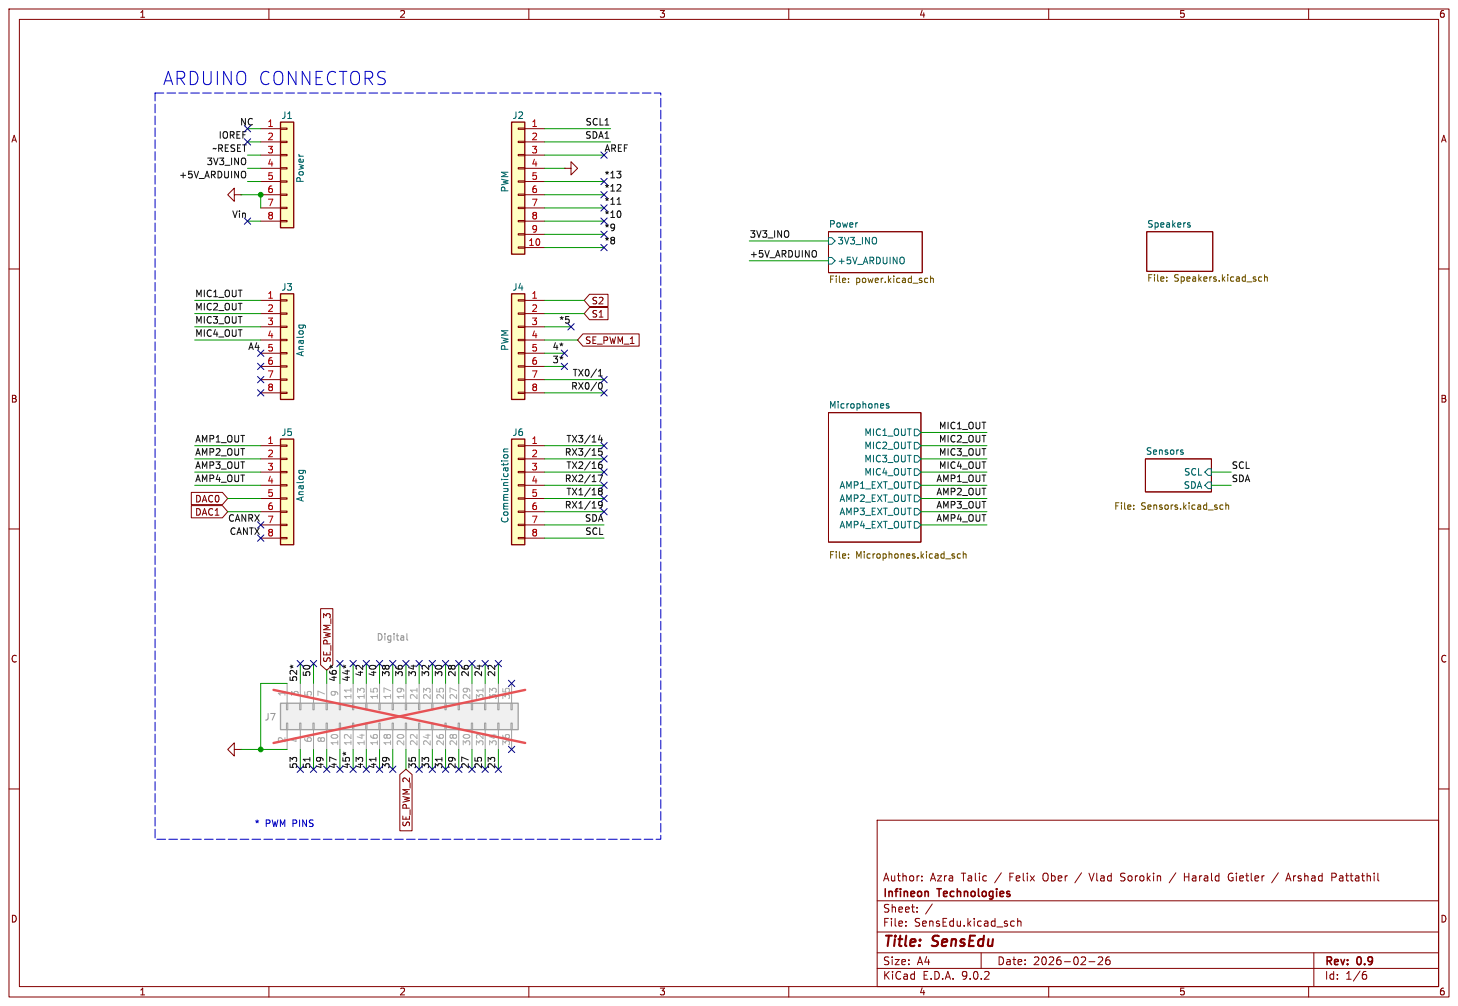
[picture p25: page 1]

* PWM PINS ARDUINO CONNECTORS

SCL Sensors File: Sensors.kicad_sch Speakers File: Speakers.kicad_sch MIC1_OUT MIC2_OUT MIC4_OUT MIC3_OUT AMP3_EXT_OUT AMP4_EXT_OUT AMP2_EXT_OUT AMP1_EXT_OUT Microphones File: Microphones.kicad_sch +5V_ARDUINO
3V3_INO

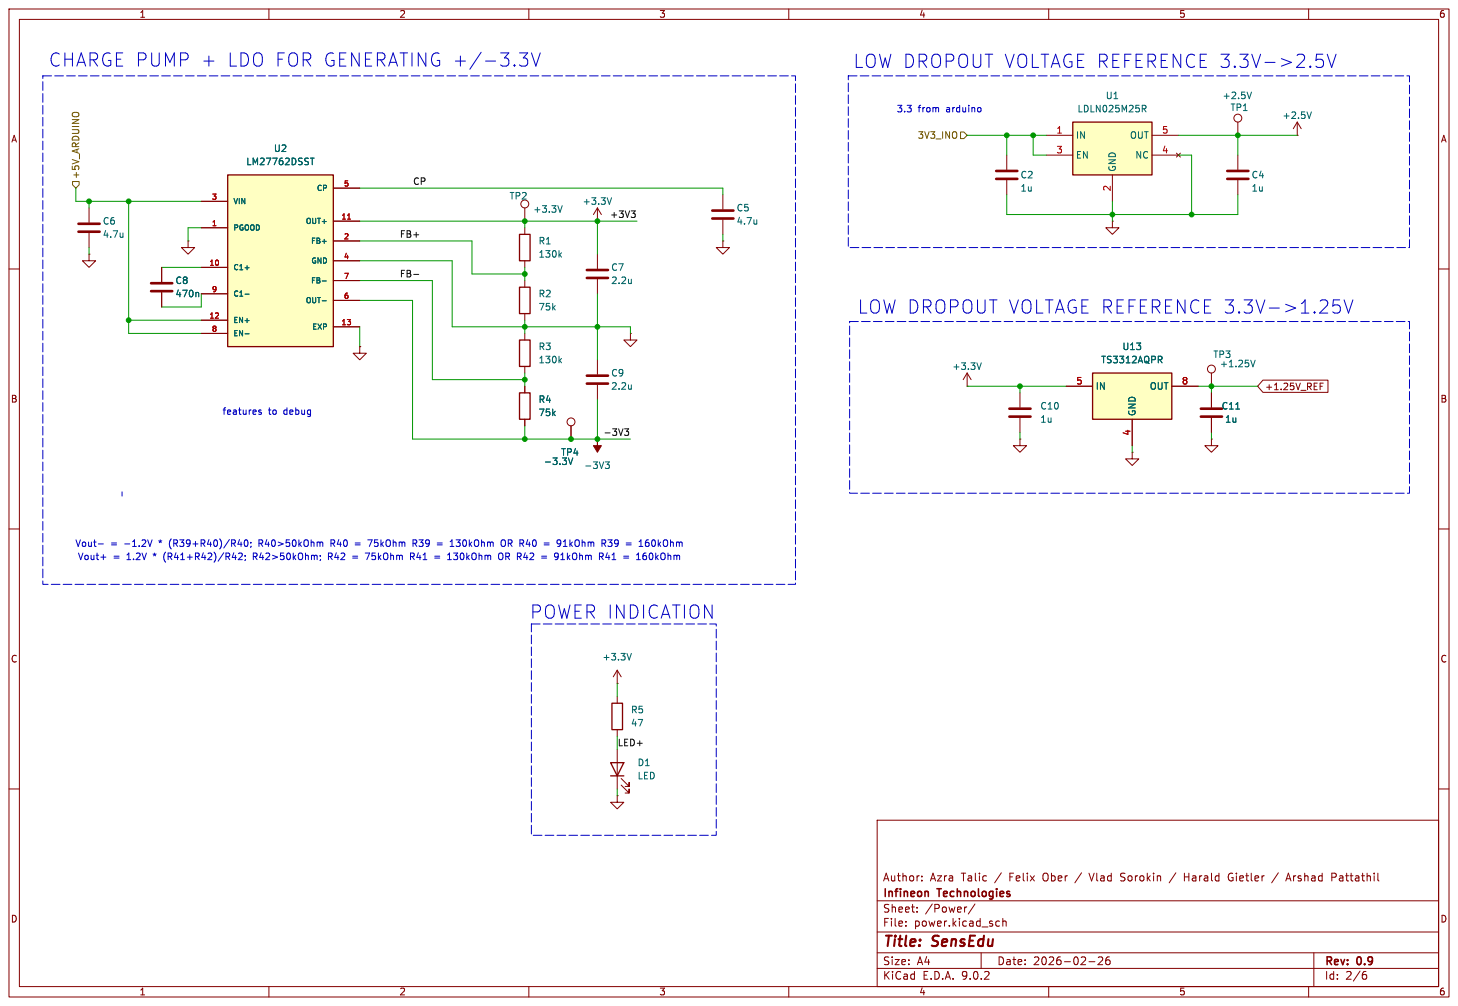
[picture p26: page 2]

LOW DROPOUT VOLTAGE REFERENCE 3.3V->1.25V

File: power.kicad_sch Sheet: /Power/
Id: 2/6 Title: SensEdu

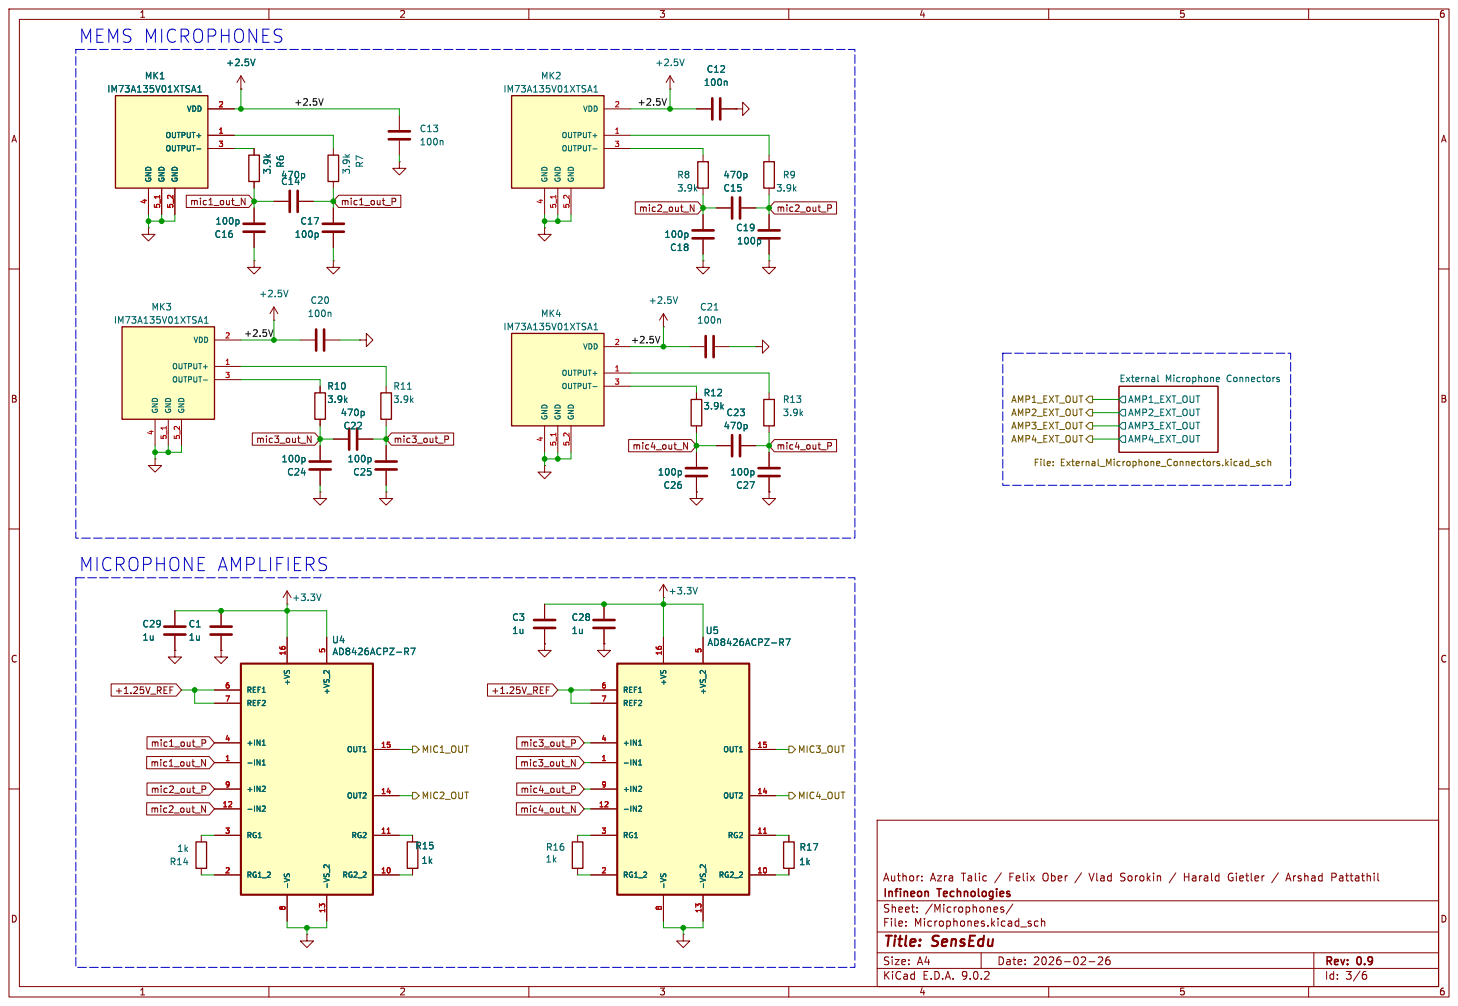
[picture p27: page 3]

4 GND 5_1 GND 5_2 VDD 2 OUTPUT+ 1 OUTPUT- 3 MK1

4 GND 5_1 GND 5_2 VDD 2 OUTPUT+ 1 OUTPUT- 3 MK2

4 GND 5_1 GND 5_2 VDD 2 OUTPUT+ 1 OUTPUT- 3 C24

4 GND 5_1 GND 5_2 VDD 2 OUTPUT+ 1 OUTPUT- 3 MK3

4 GND 5_1 GND 5_2 VDD 2 OUTPUT+ 1 OUTPUT- 3 MK4

File: Microphones.kicad_sch Sheet: /Microphones/
Id: 3/6 Title: SensEdu

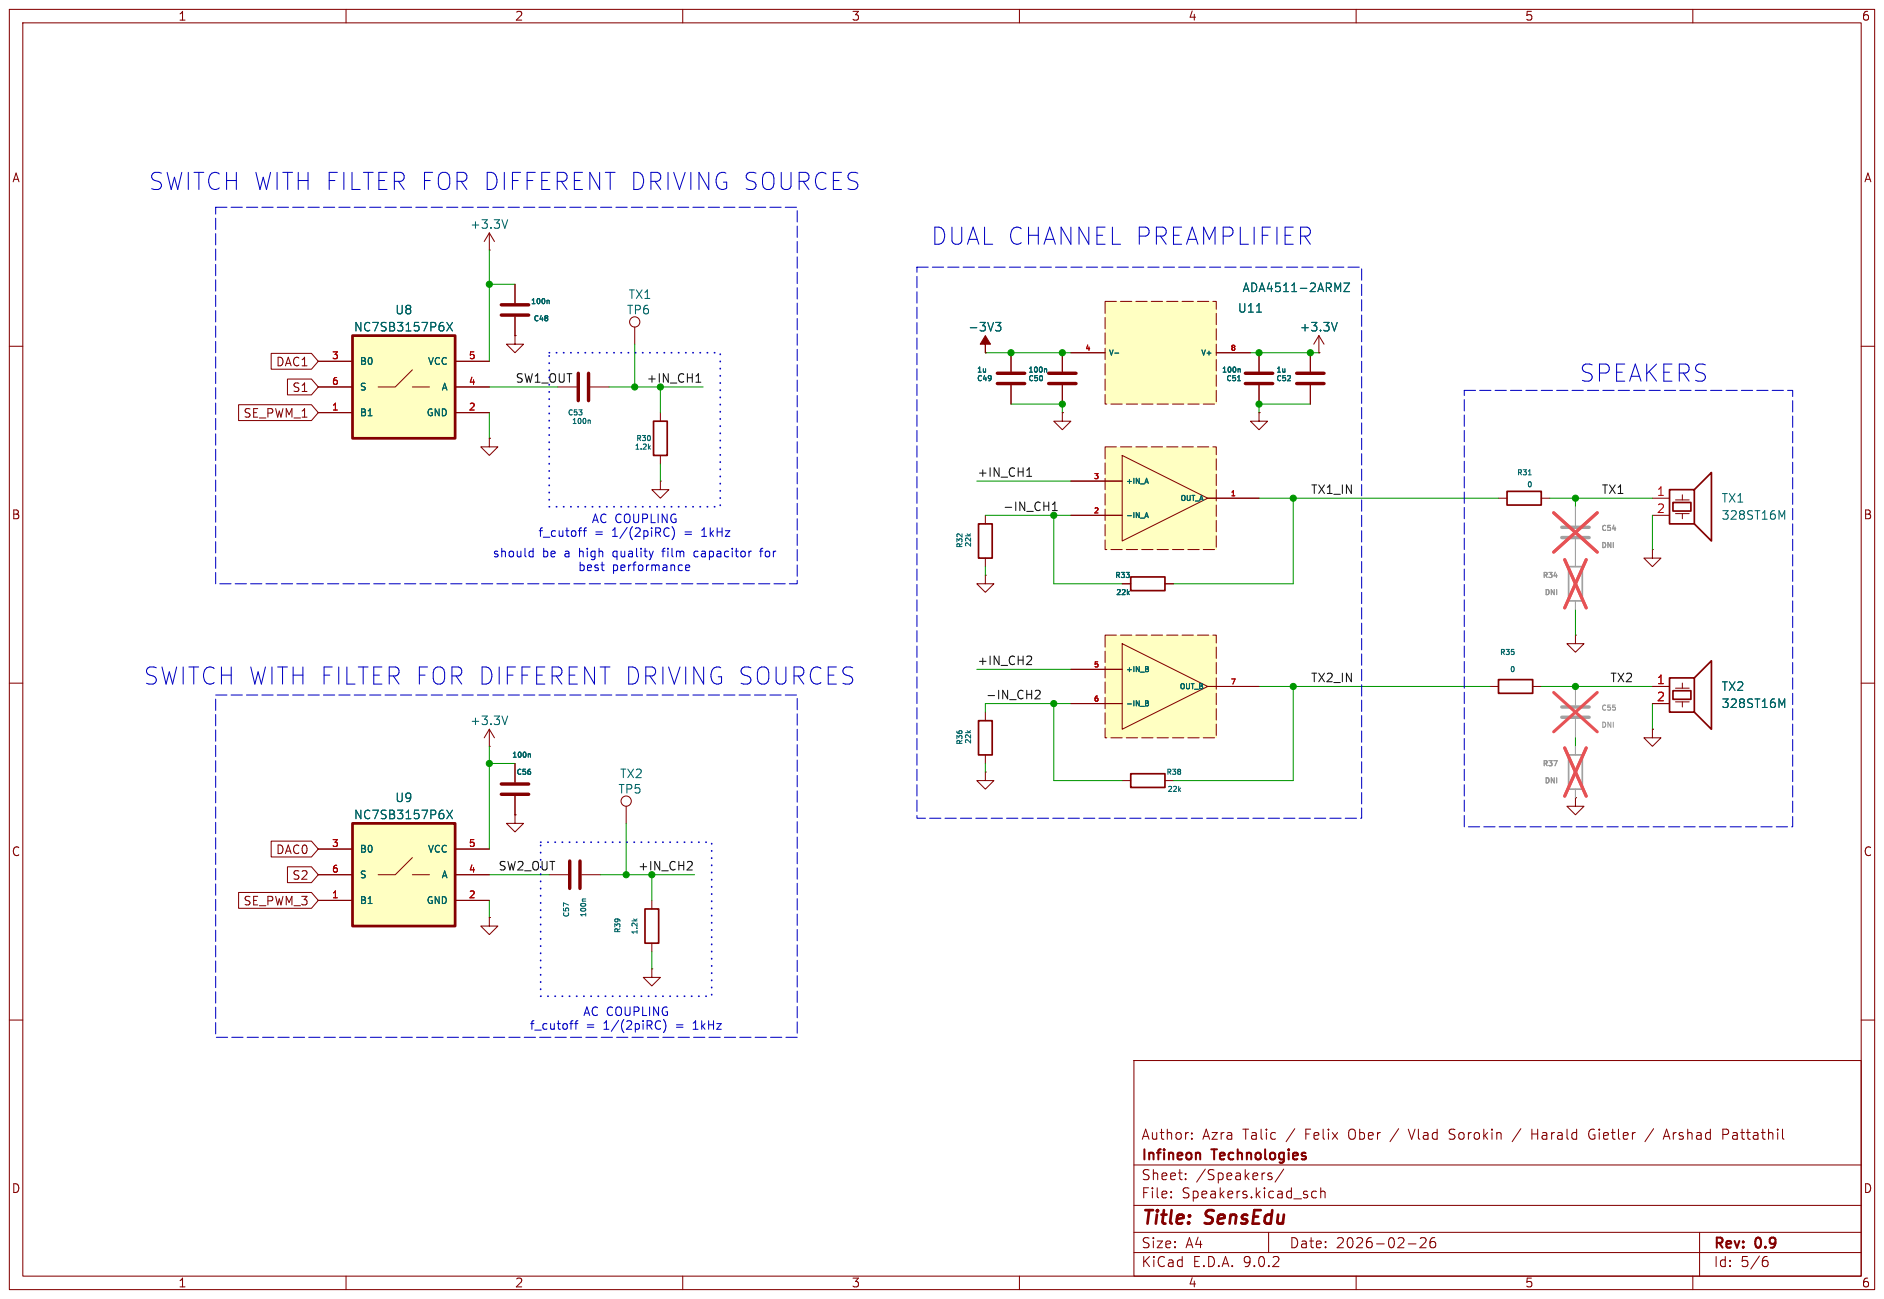
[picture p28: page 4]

SWITCH WITH FILTER FOR DIFFERENT DRIVING SOURCES

File: Speakers.kicad_sch Sheet: /Speakers/
Id: 5/6 Title: SensEdu

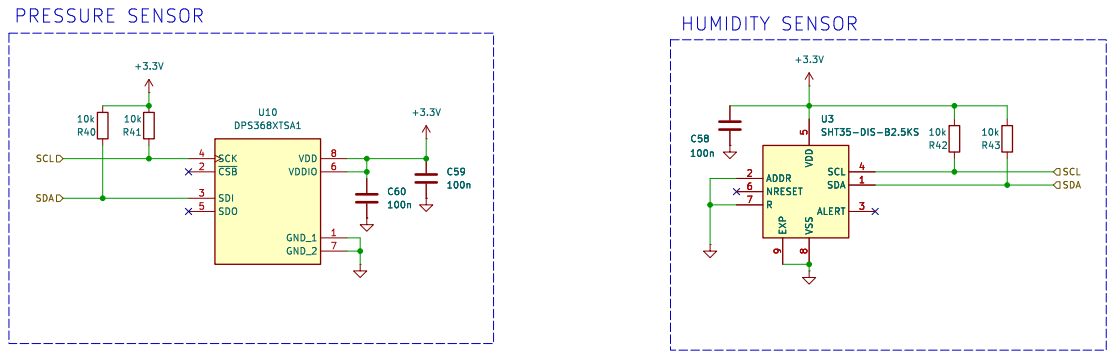
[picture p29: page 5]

8 SCL 4 SDA 1 ALERT 3 U3SHT35-DIS-B2.5KS R43

File: Sensors.kicad_sch Sheet: /Sensors/
Id: 6/6 Title: SensEdu

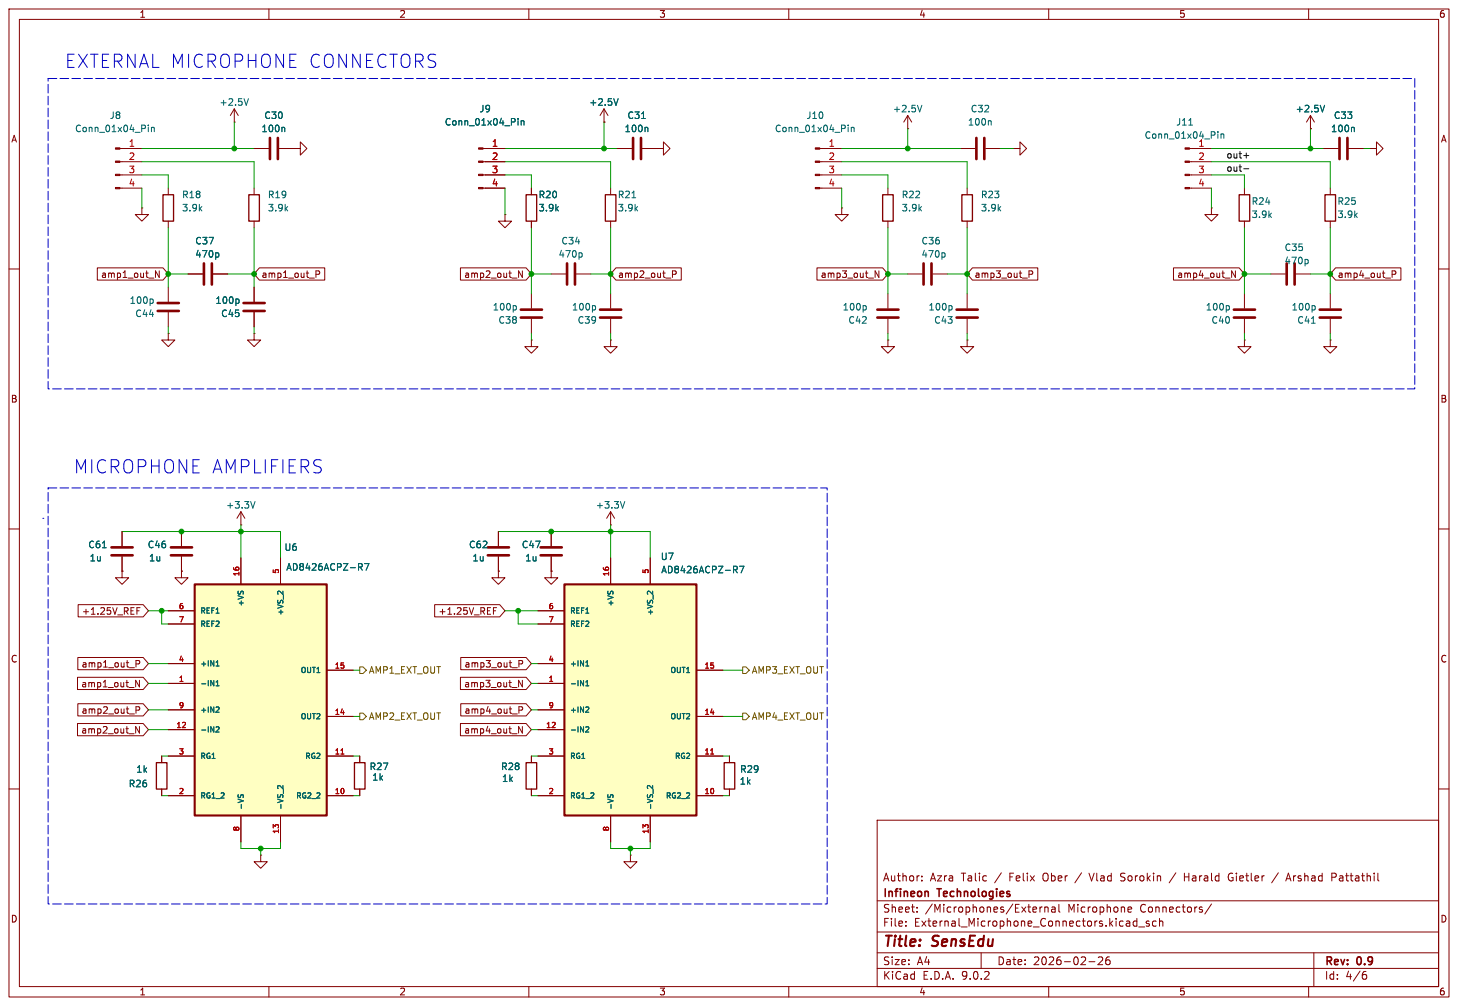
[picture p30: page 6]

out- out+ MICROPHONE AMPLIFIERS

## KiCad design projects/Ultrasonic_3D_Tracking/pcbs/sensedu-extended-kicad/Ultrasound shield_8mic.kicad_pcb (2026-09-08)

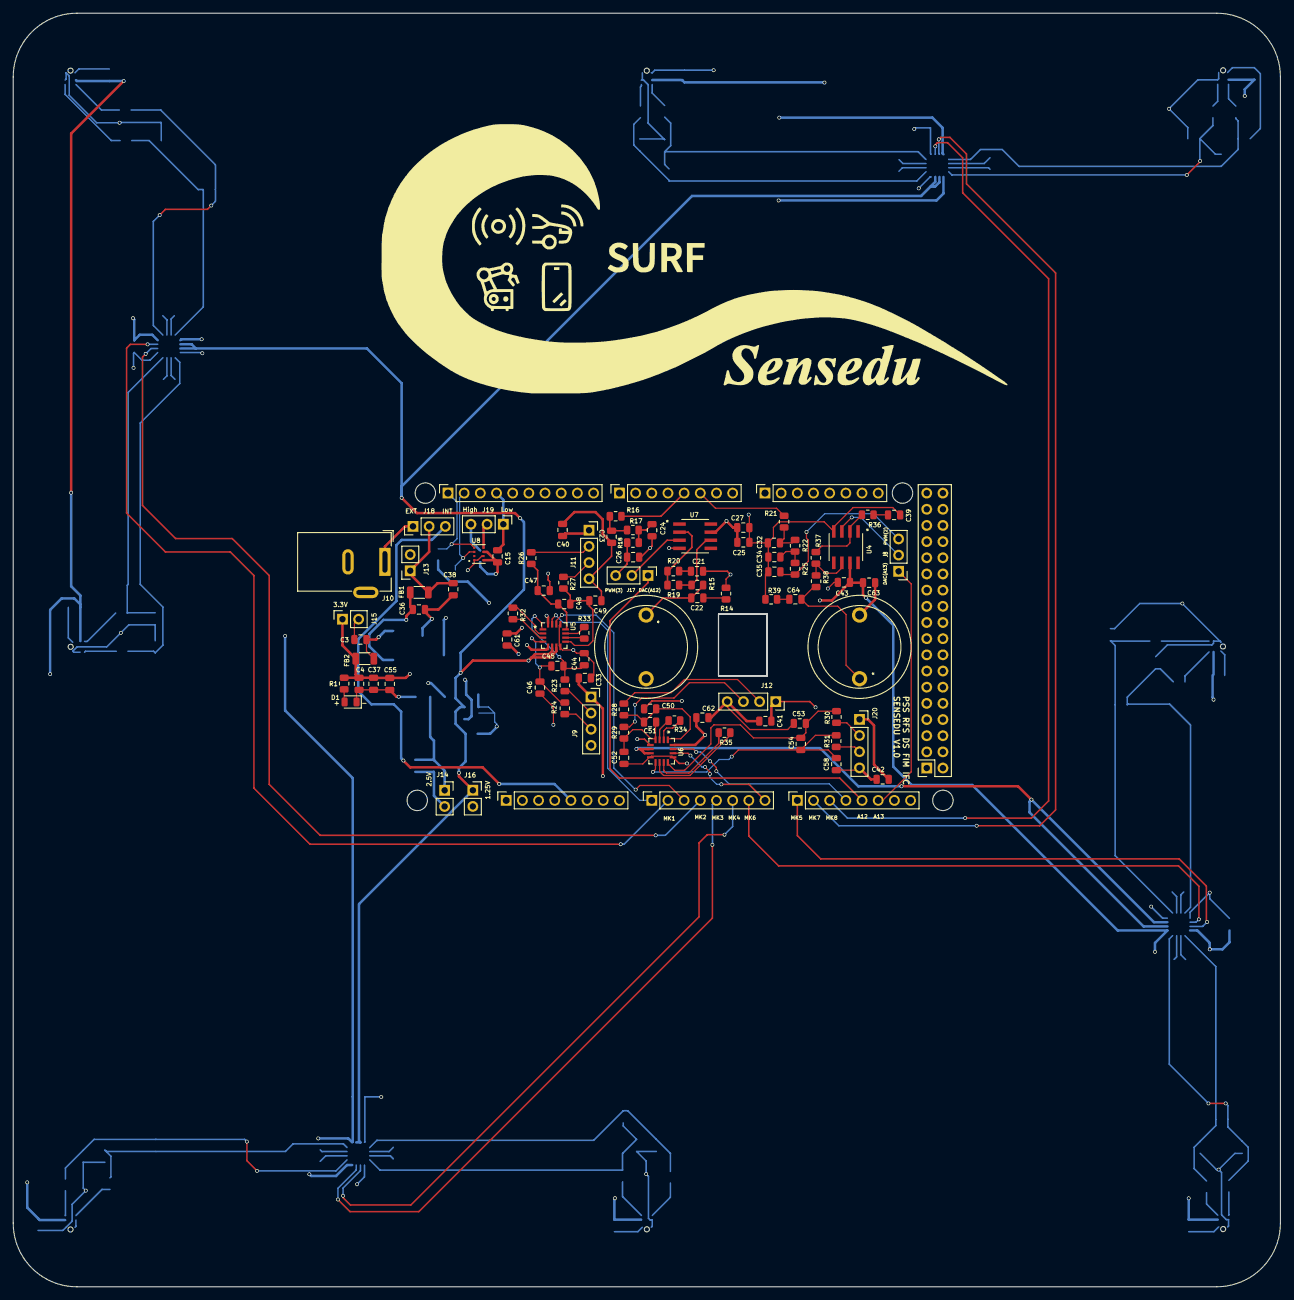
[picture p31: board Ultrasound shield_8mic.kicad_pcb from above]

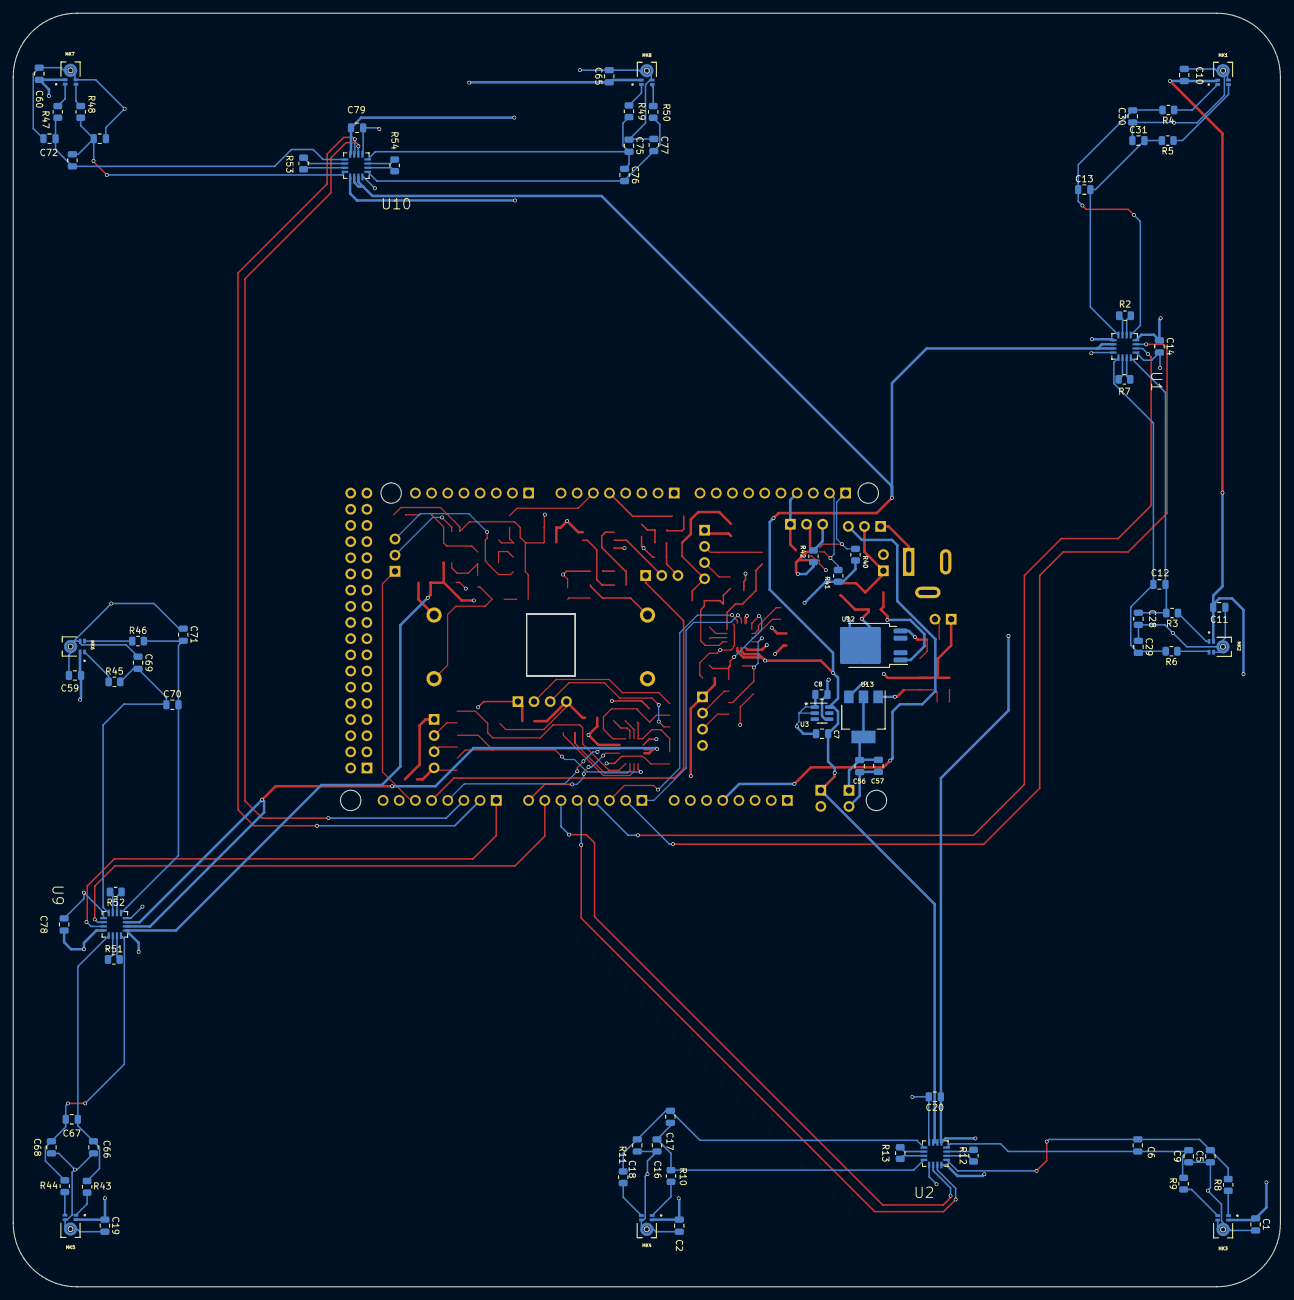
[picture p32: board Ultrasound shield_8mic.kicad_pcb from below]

Board: 4 copper layers, 199.0 x 200.0 mm, 182 parts (82 on the bottom side), 120 nets.

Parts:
C1, C2, C4, C8, C10, C11, C15, C19, C21, C27, C33, C36, C39, C40, C41, C42, C55, C57, C59, C60, C63, C65: 100n; C_0805_2012Metric
C3, C37, C38, C56: 10u; C_0805_2012Metric
C5, C9, C16, C18, C28, C29, C30, C31, C44, C46, C47, C49, C50, C52, C53, C58, C66, C68, C69, C71, C72, C74, C75, C77: 100p; C_0805_2012Metric
C6, C12, C13, C17, C45, C48, C51, C54, C67, C70, C73, C76: 470p; C_0805_2012Metric
C7, C14, C20, C25, C43, C61, C62, C78, C79: 1u; C_0805_2012Metric
C22, C64: DNI; C_0805_2012Metric
C23, C24, C26, C32, C34, C35: 1n; C_0805_2012Metric
D1: LED; LED_0805_2012Metric
FB1, FB2: FerriteBead; L_1206_3216Metric12
J1: Power; PinSocket_1x08_P2.54mm_Vertical
J2: PWM; PinSocket_1x10_P2.54mm_Vertical
J3, J5: Analog; PinSocket_1x08_P2.54mm_Vertical
J4: PWM; PinSocket_1x08_P2.54mm_Vertical
J6: Communication; PinSocket_1x08_P2.54mm_Vertical
J7: Digital; PinSocket_2x18_P2.54mm_Vertical
J8, J17, J18, J19: Conn_03x01; PinHeader_1x03_P2.54mm_Vertical
J9, J11, J12, J20: Conn_01x04_Pin; PinSocket_1x04_P2.54mm_Vertical
J10: Barrel_Jack_Switch; BarrelJack_Wuerth_6941xx301002
J13, J14, J15, J16: Conn_02x01; PinSocket_1x02_P2.54mm_Vertical
LS1, LS2: Speaker_Ultrasound; 328ST16M_Speaker
MH1, MH2, MH5, MH6: MountingHole_3.2mm
MK1, MK2, MK3, MK4, MK5, MK6, MK7, MK8: IM73A135V01XTSA1; MIC_IM73A135V01XTSA1
R1: 47; R_0805_2012Metric
R2, R7, R12, R13, R20, R32, R33, R34, R35, R36, R51, R52, R53, R54: 1k; R_0805_2012Metric
R3, R4, R5, R6, R8, R9, R10, R11, R23, R24, R26, R27, R28, R29, R30, R31, R43, R44, R45, R46, R47, R48, R49, R50: 3.9k; R_0805_2012Metric
R14, R39: DNI; R_0805_2012Metric
R15, R38: 0; R_0805_2012Metric
R16, R17, R18, R21, R22, R25: 4.7k; R_0805_2012Metric
R19, R37: 3k; R_0805_2012Metric
R40, R41, R42: 10k; R_0805_2012Metric
U1, U2, U5, U6, U9, U10: AD8426ACPZ-R7; QFN65P400X400X100-16N
U3: LT1790ACS6-1.25; TSOT-23-6
U4, U7: R_8_ADI; ADA4891-1ARZ
U8: DPS310XTSA1; XDCR_DPS310XTSA1
U12: TLS850C2TE_V33; TO-252-4
U13: NCP1117-2.5_SOT223; SOT-223-3_TabPin2

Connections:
+1.25V_REF: C7.2, J16.1, U1.6 (REF1), U1.7 (REF2), U2.6 (REF1), U2.7 (REF2), U3.6 (Vout), U5.6 (REF1), U5.7 (REF2), U6.6 (REF1), U6.7 (REF2), U9.6 (REF1), U9.7 (REF2), U10.6 (REF1), U10.7 (REF2)
+2.5V: C1.1, C2.1, C10.1, C11.1, C19.1, C33.1, C40.1, C41.1, C42.1, C56.1, C57.1, C59.1, C60.1, C65.1, J9.1, J11.1, J12.1, J14.1, J20.1, MK1.2 (VDD), MK2.2 (VDD), MK3.2 (VDD), MK4.2 (VDD), MK5.2 (VDD), MK6.2 (VDD), MK7.2 (VDD), MK8.2 (VDD), U13.2 (VO)
+3.3V: C4.1, C8.1, C14.1, C15.1, C20.1, C25.2, C27.2, C37.1, C43.2, C55.1, C61.1, C62.1, C63.2, C78.1, C79.1, FB2.2, J15.1, R1.1, R40.2, R41.1, R42.2, U1.5 (+VS), U1.16 (+VS), U2.5 (+VS), U2.16 (+VS), U3.4 (Vin), U4.7 (VS+), U5.5 (+VS), U5.16 (+VS), U6.5 (+VS), U6.16 (+VS), U7.7 (VS+), U8.6 (VDDIO), U8.8 (VDD), U9.5 (+VS), U9.16 (+VS), U10.5 (+VS), U10.16 (+VS), U13.3 (VI)
/*2: J4.6, R21.2
/*3: J4.5, R16.2
/A0: J3.1, U5.15 (OUT1)
/A1: J3.2, U1.15 (OUT1)
/A2: J3.3, U5.14 (OUT2)
/A3: J3.4, U1.14 (OUT2)
/A4: J3.5, U2.15 (OUT1)
/A5: J3.6, U2.14 (OUT2)
/A6: J3.7, U9.14 (OUT2)
/A7: J3.8, U6.14 (OUT2)
/A8: J5.1, U9.15 (OUT1)
/A9: J5.2, U10.15 (OUT1)
/A10: J5.3, U10.14 (OUT2)
/A11: J5.4, U6.15 (OUT1)
/SCL1: J2.1, R40.1, U8.4 (SCK)
/SDA1: J2.2, R41.2, U8.3 (SDI)
A12: J5.5, J17.1 (A)
A13: J5.6, J8.1 (A)
GND: C1.2, C2.2, C3.2, C4.2, C5.1, C7.1, C8.2, C9.1, C10.2, C11.2, C14.2, C15.2, C16.1, C18.1, C19.2, C20.2, C21.2, C23.2, C24.2, C25.1, C26.2, C27.1, C28.1, C29.1, C30.1, C31.1, C32.2, C33.2, C34.2, C35.2, C36.2, C37.2, C38.2, C39.2, C40.2, C41.2, C42.2, C43.1, C44.1, C46.1, C47.1, C49.1, C50.1, C52.1, C53.1, C55.2, C56.2, C57.2, C58.1, C59.2, C60.2, C61.2, C62.2, C63.1, C65.2, C66.1, C68.1, C69.1, C71.1, C72.1, C74.1, C75.1, C77.1, C78.2, C79.2, D1.1 (K), J1.6, J1.7, J2.4, J7.1, J7.2, J9.4, J10.2, J11.4, J12.4, J13.2, J14.2, J15.2, J16.2, J19.1 (A), J20.4, LS1.2, LS2.2, MK1.4 (GND), MK1.5_1 (GND), MK1.5_2 (GND), MK2.4 (GND), MK2.5_1 (GND), MK2.5_2 (GND), MK3.4 (GND), MK3.5_1 (GND), MK3.5_2 (GND), MK4.4 (GND), MK4.5_1 (GND), MK4.5_2 (GND), MK5.4 (GND), MK5.5_1 (GND), MK5.5_2 (GND), MK6.4 (GND), MK6.5_1 (GND), MK6.5_2 (GND), MK7.4 (GND), MK7.5_1 (GND), MK7.5_2 (GND), MK8.4 (GND), MK8.5_1 (GND), MK8.5_2 (GND), R14.1, R39.1, U1.8 (-VS), U1.13 (-VS), U2.8 (-VS), U2.13 (-VS), U3.1 (GND), U3.2 (GND), U4.4 (VS-), U5.8 (-VS), U5.13 (-VS), U6.8 (-VS), U6.13 (-VS), U7.4 (VS-), U8.1 (GND), U8.7 (GND), U9.8 (-VS), U9.13 (-VS), U10.8 (-VS), U10.13 (-VS), U12.3 (GND), U13.1 (GND)
unnamed: C21.1, R20.2
unnamed: C22.1, LS1.1, R15.2
unnamed: C22.2, R14.2
unnamed: C23.1, R16.1, R17.1
unnamed: C24.1, R17.2, R18.1
unnamed: C32.1, R21.1, R22.1
unnamed: C34.1, R22.2, R25.1
unnamed: C39.1, R36.2
unnamed: C64.1, LS2.1, R38.2
unnamed: C64.2, R39.2
unnamed: D1.2 (A), R1.2
unnamed: J1.5, J18.3 (B)
unnamed: C35.1, J8.3 (B), R25.2
unnamed: J8.2 (C), U4.3 (IN+)
unnamed: J9.2, R23.1
unnamed: J9.3, R24.1
unnamed: J11.2, R26.1
unnamed: J11.3, R27.1
unnamed: J12.2, R28.1
unnamed: J12.3, R29.1
unnamed: C38.1, FB1.1, J13.1, J18.2 (C)
unnamed: C26.1, J17.3 (B), R18.2
unnamed: J17.2 (C), U7.3 (IN+)
unnamed: J10.1, J18.1 (A)
unnamed: J19.3 (B), R42.1
unnamed: J19.2 (C), U8.5 (SDO)
unnamed: J20.2, R30.1
unnamed: J20.3, R31.1
unnamed: MK1.1 (OUTPUT+), R4.1
unnamed: MK1.3 (OUTPUT-), R5.1
unnamed: MK2.1 (OUTPUT+), R3.1
unnamed: MK2.3 (OUTPUT-), R6.1
unnamed: MK3.1 (OUTPUT+), R8.1
unnamed: MK3.3 (OUTPUT-), R9.1
unnamed: MK4.1 (OUTPUT+), R10.1
unnamed: MK4.3 (OUTPUT-), R11.1
unnamed: MK5.1 (OUTPUT+), R43.1
unnamed: MK5.3 (OUTPUT-), R44.1
unnamed: MK6.1 (OUTPUT+), R45.1
unnamed: MK6.3 (OUTPUT-), R46.1
unnamed: MK7.1 (OUTPUT+), R47.1
unnamed: MK7.3 (OUTPUT-), R48.1
unnamed: MK8.1 (OUTPUT+), R49.1
unnamed: MK8.3 (OUTPUT-), R50.1
unnamed: R2.1, U1.2 (RG1)
unnamed: R2.2, U1.3 (RG1)
unnamed: R7.1, U1.10 (RG2)
unnamed: R7.2, U1.11 (RG2)
unnamed: R12.1, U2.2 (RG1)
unnamed: R12.2, U2.3 (RG1)
unnamed: R13.1, U2.10 (RG2)
unnamed: R13.2, U2.11 (RG2)
unnamed: R32.1, U5.2 (RG1)
unnamed: R32.2, U5.3 (RG1)
unnamed: R33.1, U5.10 (RG2)
unnamed: R33.2, U5.11 (RG2)
unnamed: R34.1, U6.2 (RG1)
unnamed: R34.2, U6.3 (RG1)
unnamed: R35.1, U6.10 (RG2)
unnamed: R35.2, U6.11 (RG2)
unnamed: R51.1, U9.2 (RG1)
unnamed: R51.2, U9.3 (RG1)
unnamed: R52.1, U9.10 (RG2)
unnamed: R52.2, U9.11 (RG2)
unnamed: R53.1, U10.2 (RG1)
unnamed: R53.2, U10.3 (RG1)
unnamed: R54.1, U10.10 (RG2)
unnamed: R54.2, U10.11 (RG2)
unnamed: C13.2, C31.2, R5.2, U1.4 (+IN1)
unnamed: C12.2, C29.2, R6.2, U1.9 (+IN2)
unnamed: C13.1, C30.2, R4.2, U1.1 (-IN1)
unnamed: C12.1, C28.2, R3.2, U1.12 (-IN2)
unnamed: C6.2, C9.2, R9.2, U2.4 (+IN1)
unnamed: C17.2, C18.2, R11.2, U2.9 (+IN2)
unnamed: C5.2, C6.1, R8.2, U2.1 (-IN1)
unnamed: C16.2, C17.1, R10.2, U2.12 (-IN2)
unnamed: R36.1, R37.1, U4.2 (IN-)
unnamed: R37.2, R38.1, U4.6 (OUT)
unnamed: C45.2, C46.2, R24.2, U5.4 (+IN1)
unnamed: C48.2, C49.2, R27.2, U5.9 (+IN2)
unnamed: C44.2, C45.1, R23.2, U5.1 (-IN1)
unnamed: C47.2, C48.1, R26.2, U5.12 (-IN2)
unnamed: C51.2, C52.2, R29.2, U6.4 (+IN1)
unnamed: C54.2, C58.2, R31.2, U6.9 (+IN2)
unnamed: C50.2, C51.1, R28.2, U6.1 (-IN1)
unnamed: C53.2, C54.1, R30.2, U6.12 (-IN2)
unnamed: R19.1, R20.1, U7.2 (IN-)
unnamed: R15.1, R19.2, U7.6 (OUT)
unnamed: C67.2, C68.2, R44.2, U9.4 (+IN1)
unnamed: C70.2, C71.2, R46.2, U9.9 (+IN2)
unnamed: C66.2, C67.1, R43.2, U9.1 (-IN1)
unnamed: C69.2, C70.1, R45.2, U9.12 (-IN2)
unnamed: C73.2, C74.2, R48.2, U10.4 (+IN1)
unnamed: C76.2, C77.2, R50.2, U10.9 (+IN2)
unnamed: C72.2, C73.1, R47.2, U10.1 (-IN1)
unnamed: C75.2, C76.1, R49.2, U10.12 (-IN2)
unnamed: C36.1, FB1.2, U12.1 (I)
unnamed: C3.1, FB2.1, U12.5 (Q)

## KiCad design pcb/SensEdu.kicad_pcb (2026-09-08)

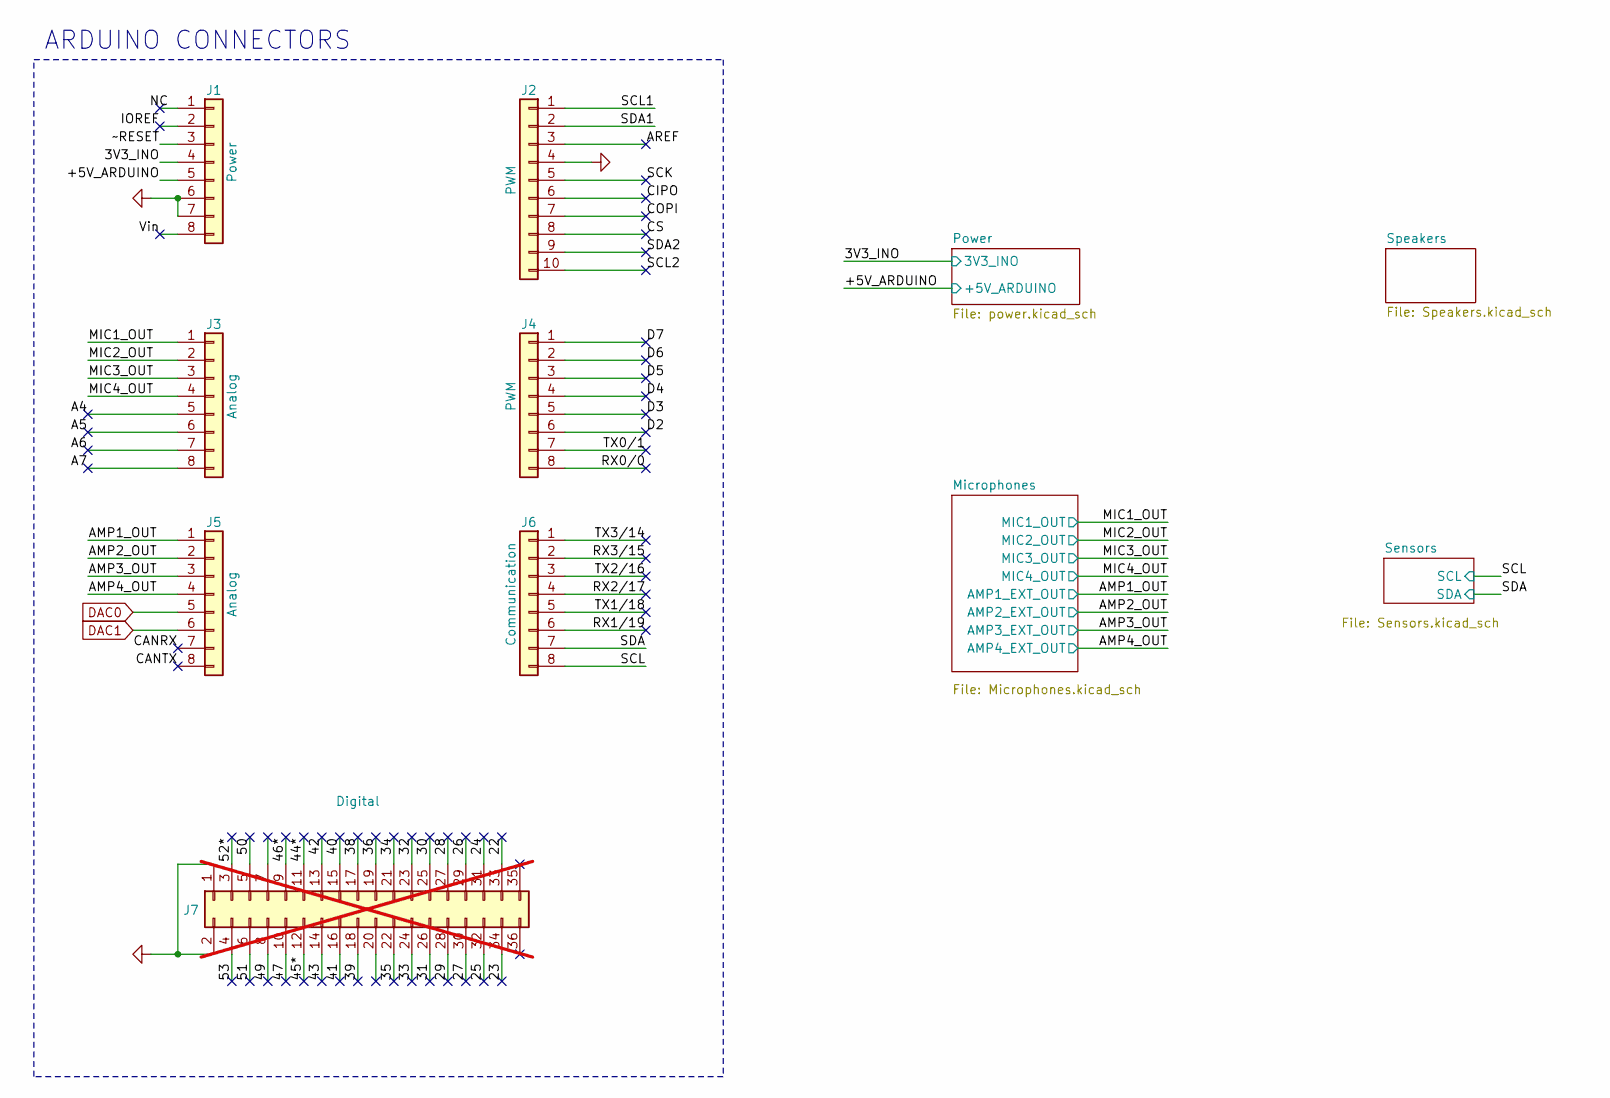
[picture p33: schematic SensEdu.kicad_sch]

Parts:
J1: Power; PinSocket_1x08_P2.54mm_Vertical
J2: PWM; PinSocket_1x10_P2.54mm_Vertical
J3, J5: Analog; PinSocket_1x08_P2.54mm_Vertical
J4: PWM; PinSocket_1x08_P2.54mm_Vertical
J6: Communication; PinSocket_1x08_P2.54mm_Vertical
J7: Digital; PinSocket_2x18_P2.54mm_Vertical; not fitted

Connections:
/3V3_INO: J1.4; also elsewhere on the board
/22: J7.33
/23: J7.34
/24: J7.31
/25: J7.32
/26: J7.29
/27: J7.30
/28: J7.27
/29: J7.28
/30: J7.25
/31: J7.26
/32: J7.23
/33: J7.24
/34: J7.21
/35: J7.22
/36: J7.19
/38: J7.17
/39: J7.18
/40: J7.15
/41: J7.16
/42: J7.13
/43: J7.14
/44*: J7.11
/45*: J7.12
/46*: J7.9
/47: J7.10
/49: J7.8
/50: J7.5
/51: J7.6
/52*: J7.3
/53: J7.4
/+5V_ARDUINO: J1.5; also elsewhere on the board
/A4: J3.5
/A5: J3.6
/A6: J3.7
/A7: J3.8
/AMP1_OUT: J5.1; also elsewhere on the board
/AMP2_OUT: J5.2; also elsewhere on the board
/AMP3_OUT: J5.3; also elsewhere on the board
/AMP4_OUT: J5.4; also elsewhere on the board
/AREF: J2.3
/CANRX: J5.7
/CANTX: J5.8
/CIPO: J2.6
/COPI: J2.7
/CS: J2.8
/D2: J4.6
/D3: J4.5
/D4: J4.4
/D5: J4.3
/D6: J4.2
/D7: J4.1
/IOREF: J1.2
/MIC1_OUT: J3.1; also elsewhere on the board
/MIC2_OUT: J3.2; also elsewhere on the board
/MIC3_OUT: J3.3; also elsewhere on the board
/MIC4_OUT: J3.4; also elsewhere on the board
/NC: J1.1
/RX0/0: J4.8
/RX1/19: J6.6
/RX2/17: J6.4
/RX3/15: J6.2
/SCK: J2.5
/SCL: J6.8; also elsewhere on the board
/SCL1: J2.1
/SCL2: J2.10
/SDA: J6.7; also elsewhere on the board
/SDA1: J2.2
/SDA2: J2.9
/TX0/1: J4.7
/TX1/18: J6.5
/TX2/16: J6.3
/TX3/14: J6.1
/Vin: J1.8
/~RESET: J1.3
DAC0: J5.5; also elsewhere on the board
DAC1: J5.6; also elsewhere on the board
GND: J1.6, J1.7, J2.4, J7.1, J7.2; also elsewhere on the board

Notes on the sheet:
ARDUINO CONNECTORS

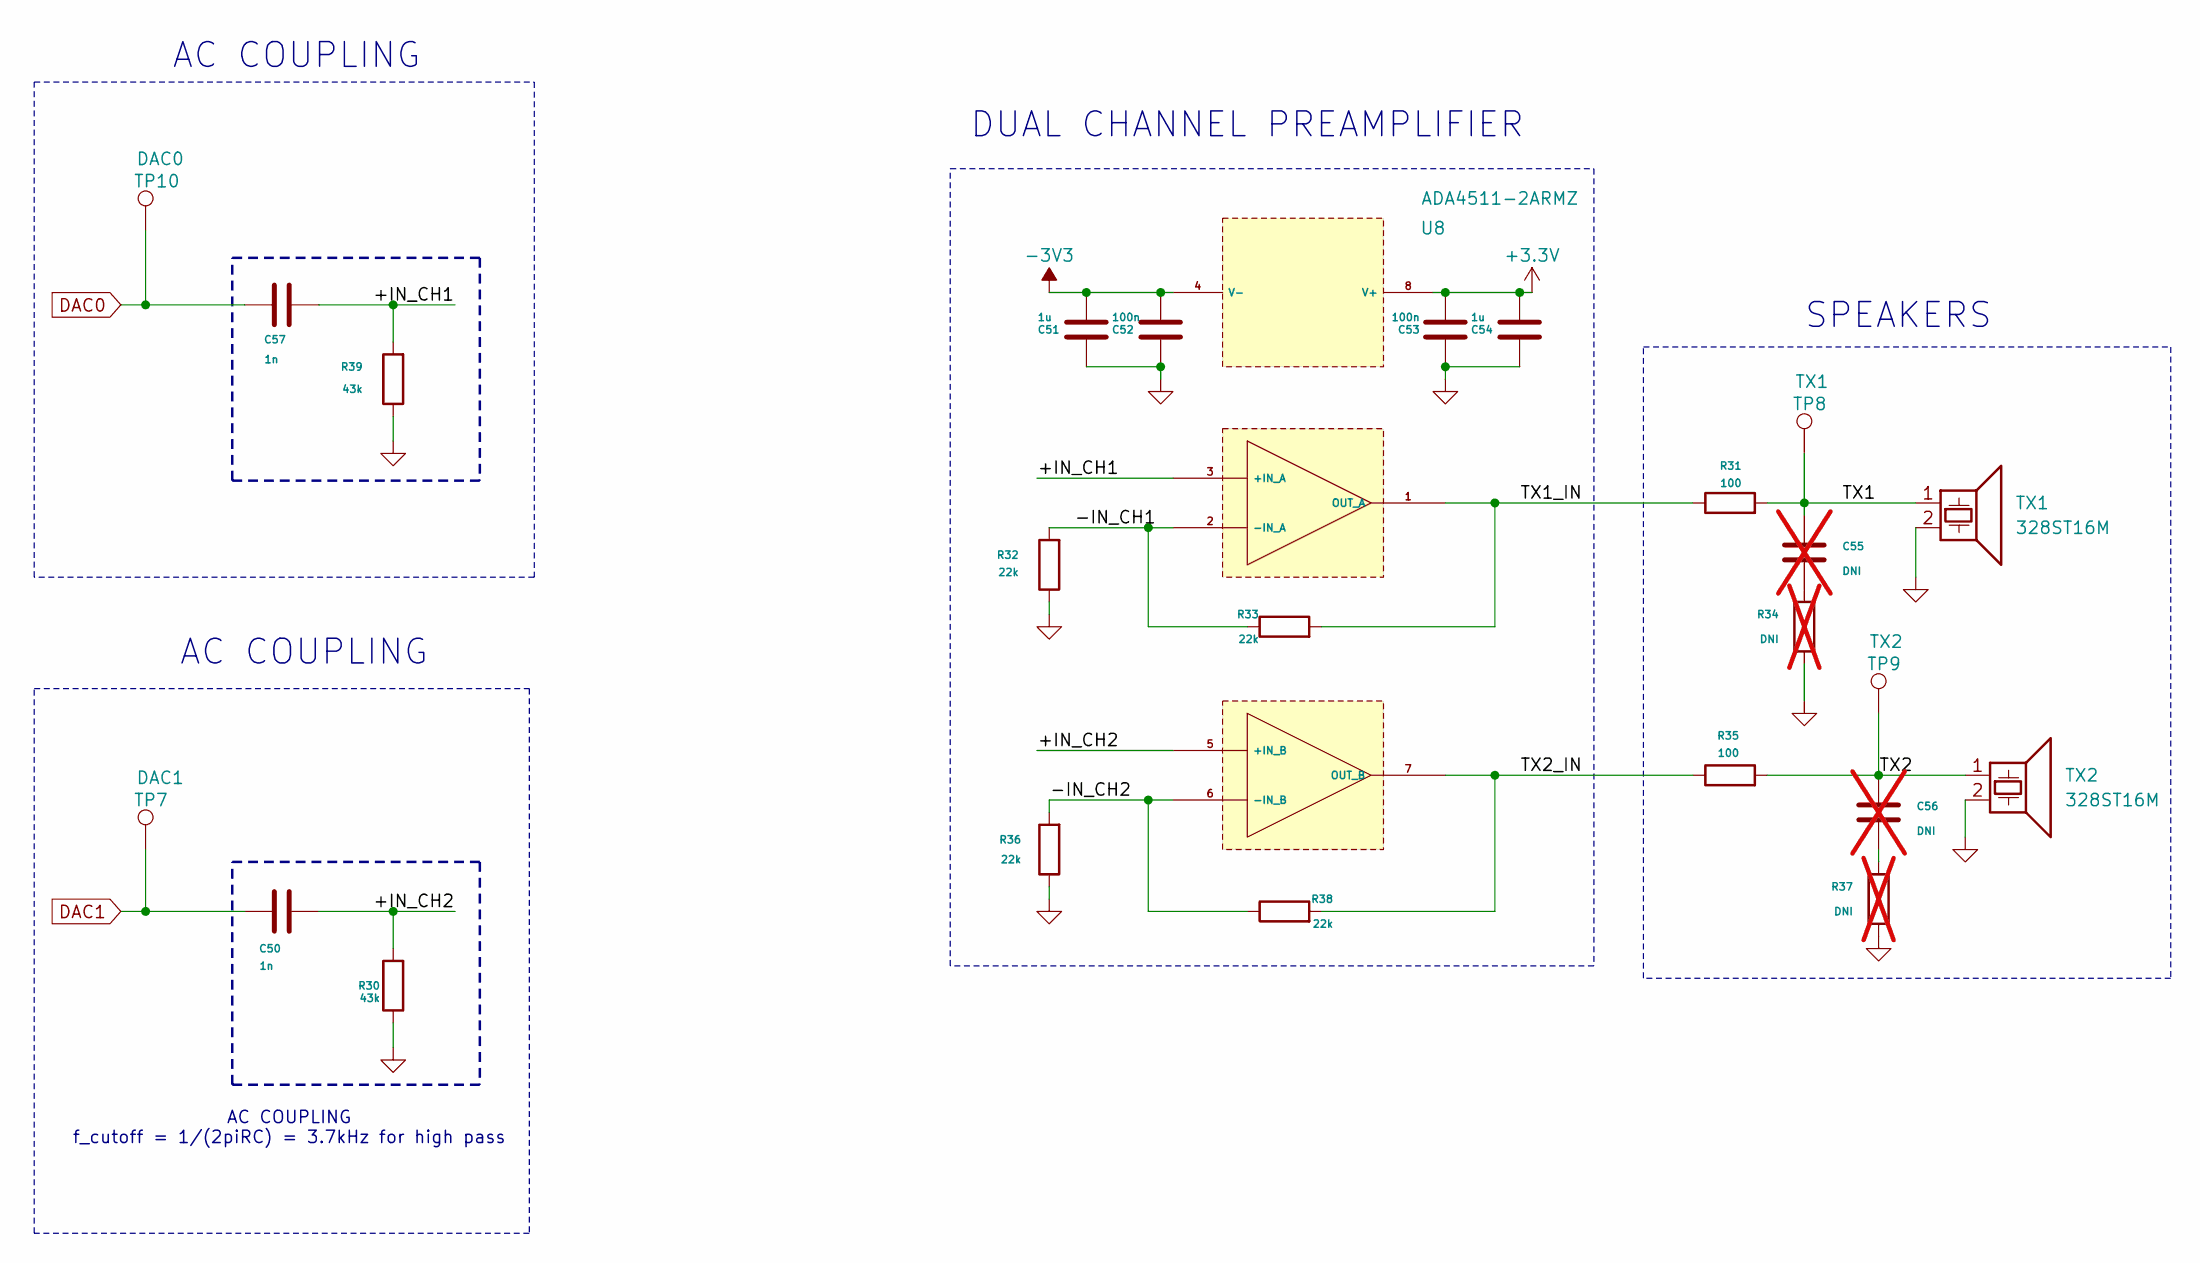
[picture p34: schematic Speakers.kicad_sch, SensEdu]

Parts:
C50, C57: 1n; C_0603_1608Metric
C51, C54: 1u; C_0603_1608Metric
C52, C53: 100n; C_0603_1608Metric
C55, C56: DNI; C_0603_1608Metric; not fitted
R30, R39: 43k; R_0603_1608Metric
R31, R35: 100; R_0603_1608Metric
R32, R33, R36, R38: 22k; R_0603_1608Metric
R34, R37: DNI; R_0603_1608Metric; not fitted
TP7: DAC1; TestPoint_THTPad_D2.0mm_Drill1.0mm
TP8: TX1; TestPoint_THTPad_D2.0mm_Drill1.0mm
TP9: TX2; TestPoint_THTPad_D2.0mm_Drill1.0mm
TP10: DAC0; TestPoint_THTPad_D2.0mm_Drill1.0mm
TX1, TX2: 328ST16M; 328ST16M_Speaker
U8: ADA4511-2ARMZ; SOP65P490X110-8N; Manufacturer_Part_Number ADA4511-2ARMZ

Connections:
+3.3V: C53.2, C54.1, U8.8 (V+); also elsewhere on the board
-3V3: C51.1, C52.1, U8.4 (V-); also elsewhere on the board
/Speakers/+IN_CH1: C57.2, R39.2, U8.3 (+IN_A)
/Speakers/+IN_CH2: C50.2, R30.2, U8.5 (+IN_B)
/Speakers/-IN_CH1: R32.2, R33.1, U8.2 (-IN_A)
/Speakers/-IN_CH2: R36.2, R38.1, U8.6 (-IN_B)
/Speakers/TX1: C55.1, R31.2, TP8.1, TX1.1
/Speakers/TX1_IN: R31.1, R33.2, U8.1 (OUT_A)
/Speakers/TX2: C56.1, R35.2, TP9.1, TX2.1
/Speakers/TX2_IN: R35.1, R38.2, U8.7 (OUT_B)
DAC0: C57.1, TP10.1; also elsewhere on the board
DAC1: C50.1, TP7.1; also elsewhere on the board
GND: C51.2, C52.2, C53.1, C54.2, R30.1, R32.1, R34.1, R36.1, R37.1, R39.1, TX1.2, TX2.2; also elsewhere on the board
unnamed: C55.2, R34.2
unnamed: C56.2, R37.2

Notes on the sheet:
AC COUPLING f_cutoff = 1/(2piRC) = 3.7kHz for high pass
AC COUPLING
SPEAKERS
DUAL CHANNEL PREAMPLIFIER
AC COUPLING

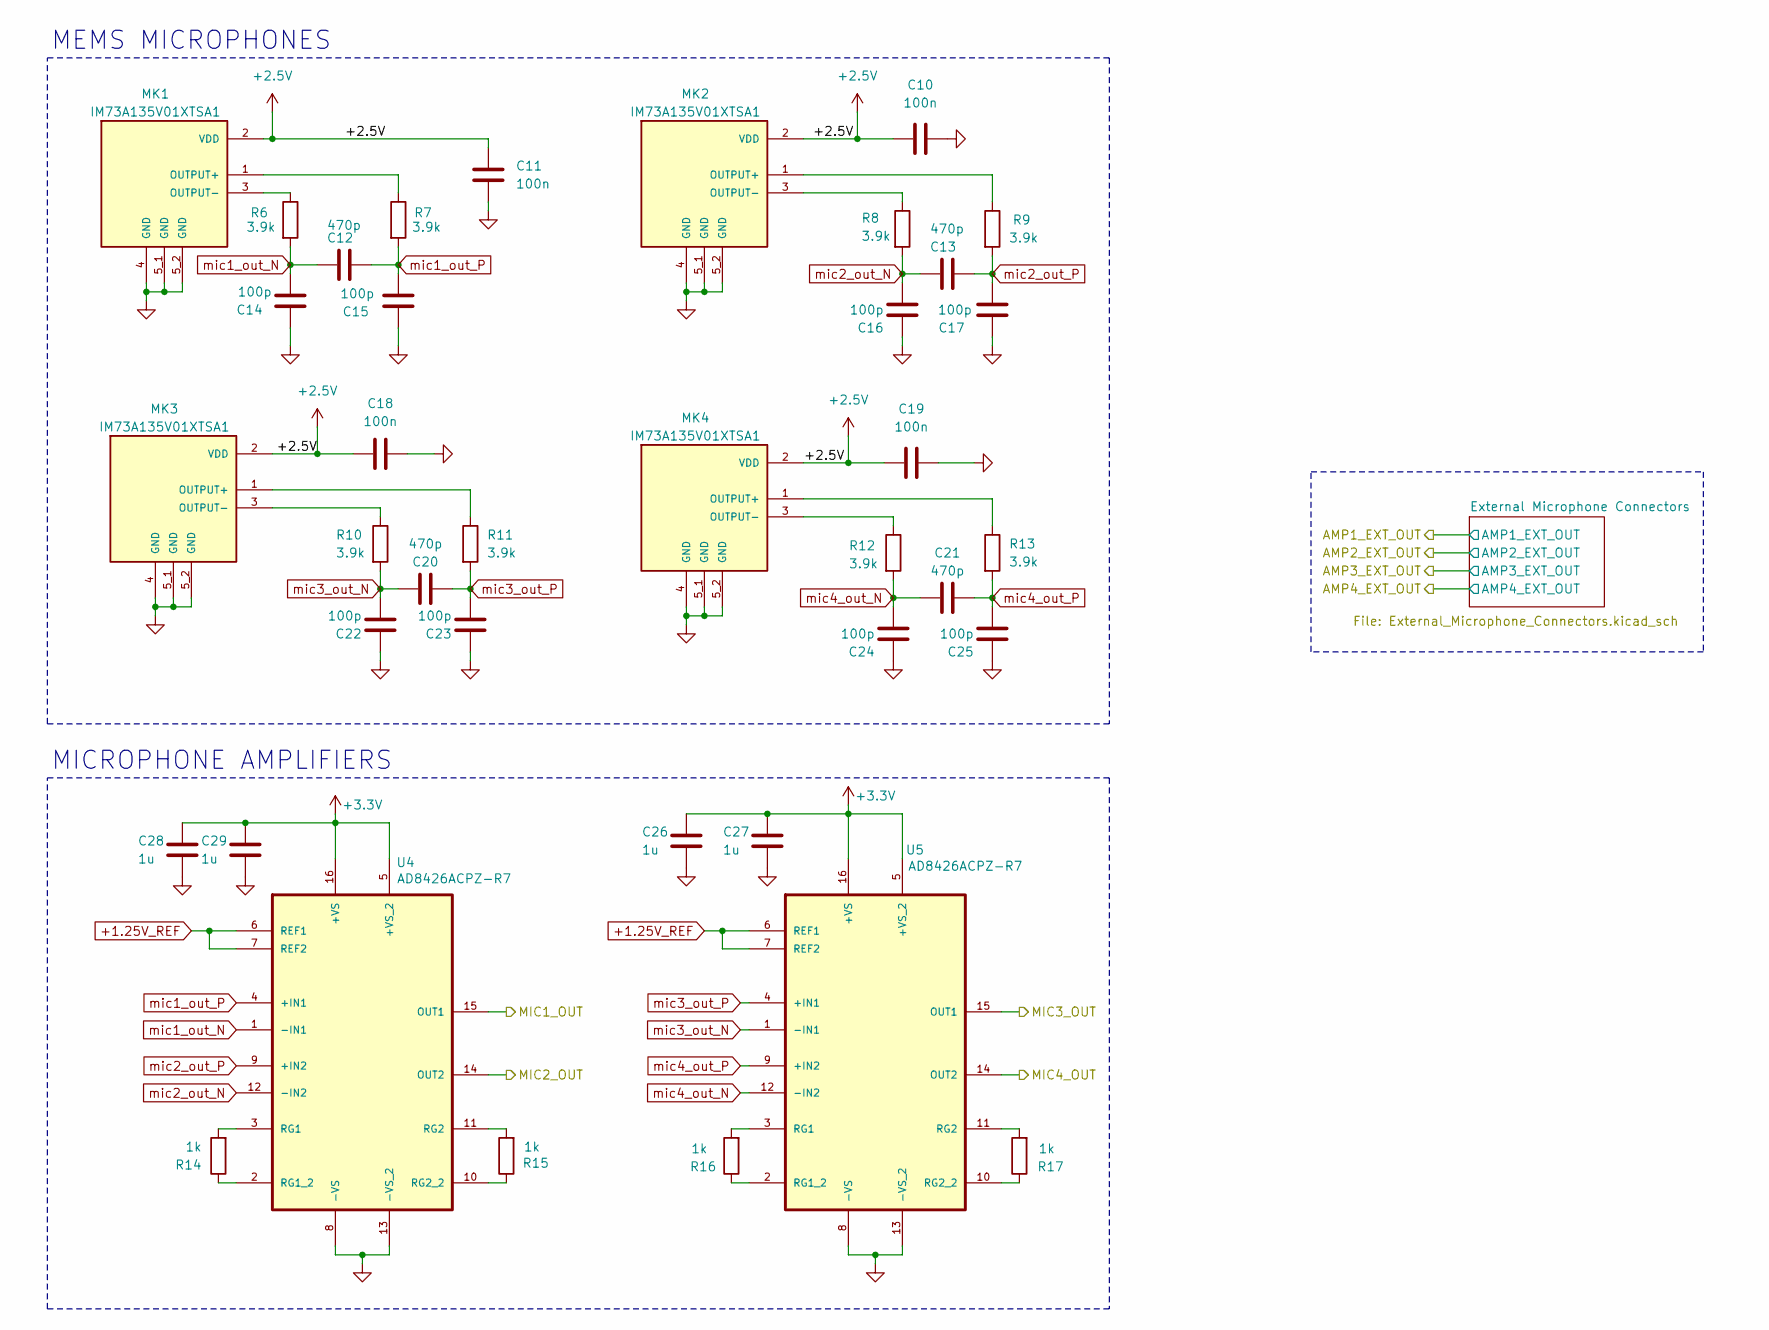
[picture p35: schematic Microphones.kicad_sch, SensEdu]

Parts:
C10, C11, C18, C19: 100n; C_0603_1608Metric
C12, C13, C20, C21: 470p; C_0603_1608Metric
C14, C15, C16, C17, C22, C23, C24, C25: 100p; C_0603_1608Metric
C26, C27, C28, C29: 1u; C_0603_1608Metric
MK1, MK2, MK3, MK4: IM73A135V01XTSA1; MIC_IM73A135V01XTSA1; PARTREV V1.20
R6, R7, R8, R9, R10, R11, R12, R13: 3.9k; R_0603_1608Metric
R14, R15, R16, R17: 1k; R_0603_1608Metric
U4, U5: AD8426ACPZ-R7; QFN65P400X400X100-16N; MPN AD8426ACPZ-R7

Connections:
+1.25V_REF: U4.6 (REF1), U4.7 (REF2), U5.6 (REF1), U5.7 (REF2); also elsewhere on the board
+2.5V: C10.1, C11.1, C18.1, C19.1, MK1.2 (VDD), MK2.2 (VDD), MK3.2 (VDD), MK4.2 (VDD); also elsewhere on the board
+3.3V: C26.1, C27.1, C28.1, C29.1, U4.5 (+VS_2), U4.16 (+VS), U5.5 (+VS_2), U5.16 (+VS); also elsewhere on the board
/MIC1_OUT: U4.15 (OUT1); also elsewhere on the board
/MIC2_OUT: U4.14 (OUT2); also elsewhere on the board
/MIC3_OUT: U5.15 (OUT1); also elsewhere on the board
/MIC4_OUT: U5.14 (OUT2); also elsewhere on the board
GND: C10.2, C11.2, C14.1, C15.1, C16.1, C17.1, C18.2, C19.2, C22.1, C23.1, C24.1, C25.1, C26.2, C27.2, C28.2, C29.2, MK1.4 (GND), MK1.5_1 (GND), MK1.5_2 (GND), MK2.4 (GND), MK2.5_1 (GND), MK2.5_2 (GND), MK3.4 (GND), MK3.5_1 (GND), MK3.5_2 (GND), MK4.4 (GND), MK4.5_1 (GND), MK4.5_2 (GND), U4.8 (-VS), U4.13 (-VS_2), U5.8 (-VS), U5.13 (-VS_2); also elsewhere on the board
unnamed: MK1.1 (OUTPUT+), R7.1
unnamed: MK1.3 (OUTPUT-), R6.1
unnamed: MK2.1 (OUTPUT+), R9.1
unnamed: MK2.3 (OUTPUT-), R8.1
unnamed: MK3.1 (OUTPUT+), R11.1
unnamed: MK3.3 (OUTPUT-), R10.1
unnamed: MK4.1 (OUTPUT+), R13.1
unnamed: MK4.3 (OUTPUT-), R12.1
unnamed: R14.2, U4.3 (RG1)
unnamed: R14.1, U4.2 (RG1_2)
unnamed: R15.2, U4.11 (RG2)
unnamed: R15.1, U4.10 (RG2_2)
unnamed: R16.2, U5.3 (RG1)
unnamed: R16.1, U5.2 (RG1_2)
unnamed: R17.2, U5.11 (RG2)
unnamed: R17.1, U5.10 (RG2_2)
mic1_out_N: C12.2, C14.2, R6.2, U4.1 (-IN1)
mic1_out_P: C12.1, C15.2, R7.2, U4.4 (+IN1)
mic2_out_N: C13.2, C16.2, R8.2, U4.12 (-IN2)
mic2_out_P: C13.1, C17.2, R9.2, U4.9 (+IN2)
mic3_out_N: C20.2, C22.2, R10.2, U5.1 (-IN1)
mic3_out_P: C20.1, C23.2, R11.2, U5.4 (+IN1)
mic4_out_N: C21.2, C24.2, R12.2, U5.12 (-IN2)
mic4_out_P: C21.1, C25.2, R13.2, U5.9 (+IN2)

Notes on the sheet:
MEMS MICROPHONES
MICROPHONE AMPLIFIERS

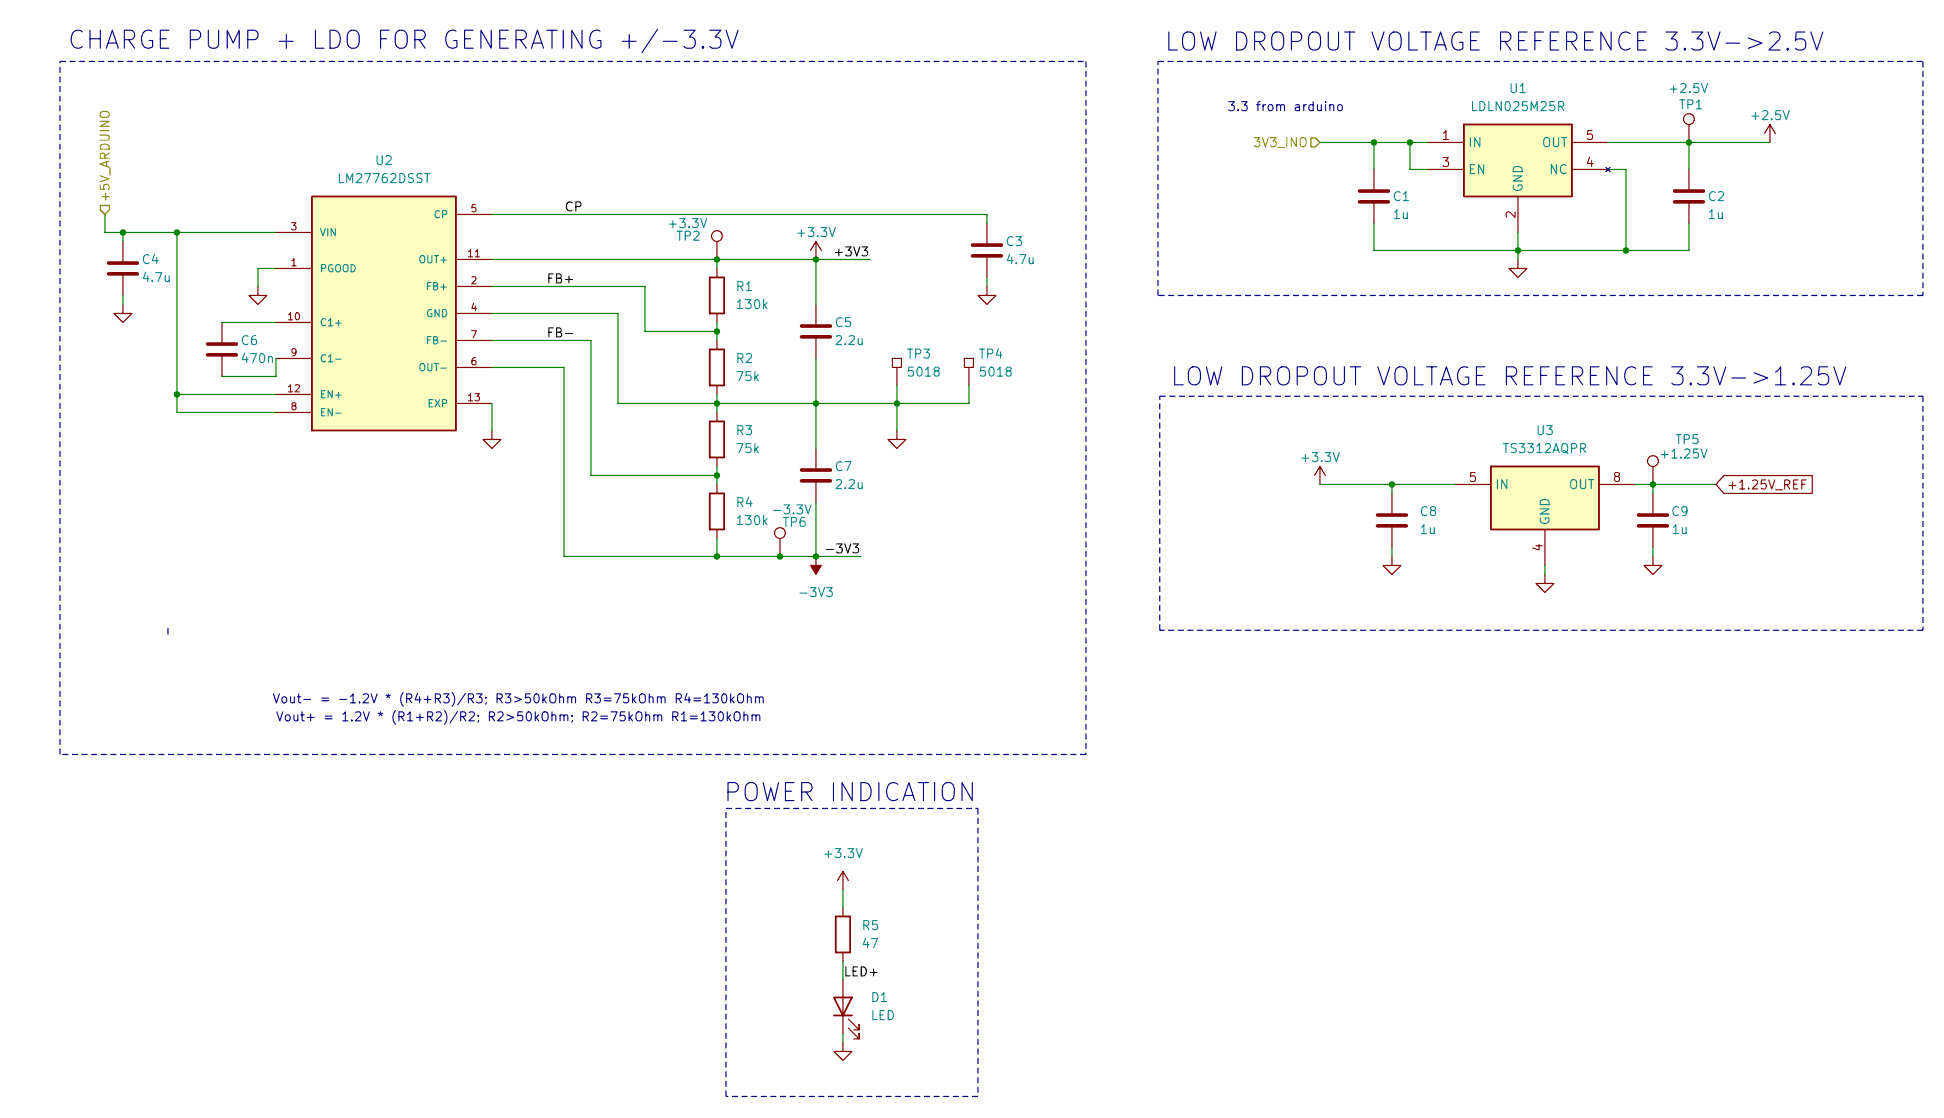
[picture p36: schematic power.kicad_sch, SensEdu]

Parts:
C1, C2, C8, C9: 1u; C_0603_1608Metric
C3, C4: 4.7u; C_0805_2012Metric
C5, C7: 2.2u; C_0805_2012Metric
C6: 470n; C_0603_1608Metric
D1: LED; LED_0805_2012Metric
R1, R4: 130k; R_0603_1608Metric
R2, R3: 75k; R_0603_1608Metric
R5: 47; R_0603_1608Metric
TP1: +2.5V; TestPoint_THTPad_D2.0mm_Drill1.0mm
TP2: +3.3V; TestPoint_THTPad_D2.0mm_Drill1.0mm
TP3, TP4: 5018; Manufacturer_Part_Number 5018; Mouser Part Number 534-5018
TP5: +1.25V; TestPoint_THTPad_D2.0mm_Drill1.0mm
TP6: -3.3V; TestPoint_THTPad_D2.0mm_Drill1.0mm
U1: LDLN025M25R; SOT95P280X145-5N; Manufacturer_Part_Number LDLN025M25R; Mouser Part Number 511-LDLN025M25R
U2: LM27762DSST; IC_LM27762DSST; PARTREV B
U3: TS3312AQPR; Manufacturer_Part_Number TS3312AQPR; Mouser Part Number 511-TS3312AQPR

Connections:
+1.25V_REF: C9.2, TP5.1, U3.8 (OUT); also elsewhere on the board
+2.5V: C2.1, TP1.1, U1.5 (OUT); also elsewhere on the board
+3.3V: C5.1, C8.1, R1.1, R5.1, TP2.1, U2.11 (OUT+), U3.5 (IN); also elsewhere on the board
-3V3: C7.2, R4.2, TP6.1, U2.6 (OUT-); also elsewhere on the board
/3V3_INO: C1.1, U1.1 (IN), U1.3 (EN); also elsewhere on the board
/+5V_ARDUINO: C4.1, U2.3 (VIN), U2.8 (EN-), U2.12 (EN+); also elsewhere on the board
/Power/CP: C3.1, U2.5 (CP)
/Power/FB+: R1.2, R2.1, U2.2 (FB+)
/Power/FB-: R3.2, R4.1, U2.7 (FB-)
/Power/LED+: D1.2 (A), R5.2
GND: C1.2, C2.2, C3.2, C4.2, C5.2, C7.1, C8.2, C9.1, D1.1 (K), R2.2, R3.1, TP3.1, TP4.1, U1.2 (GND), U1.4 (NC), U2.1 (PGOOD), U2.4 (GND), U2.13 (EXP), U3.4 (GND); also elsewhere on the board
unnamed: C6.1, U2.10 (C1+)
unnamed: C6.2, U2.9 (C1-)

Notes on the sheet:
CHARGE PUMP + LDO FOR GENERATING +/-3.3V
Vout- = -1.2V * (R4+R3)/R3; R3>50kOhm R3=75kOhm R4=130kOhm
POWER INDICATION
LOW DROPOUT VOLTAGE REFERENCE 3.3V->1.25V
Vout+ = 1.2V * (R1+R2)/R2; R2>50kOhm; R2=75kOhm R1=130kOhm
LOW DROPOUT VOLTAGE REFERENCE 3.3V->2.5V
3.3 from arduino

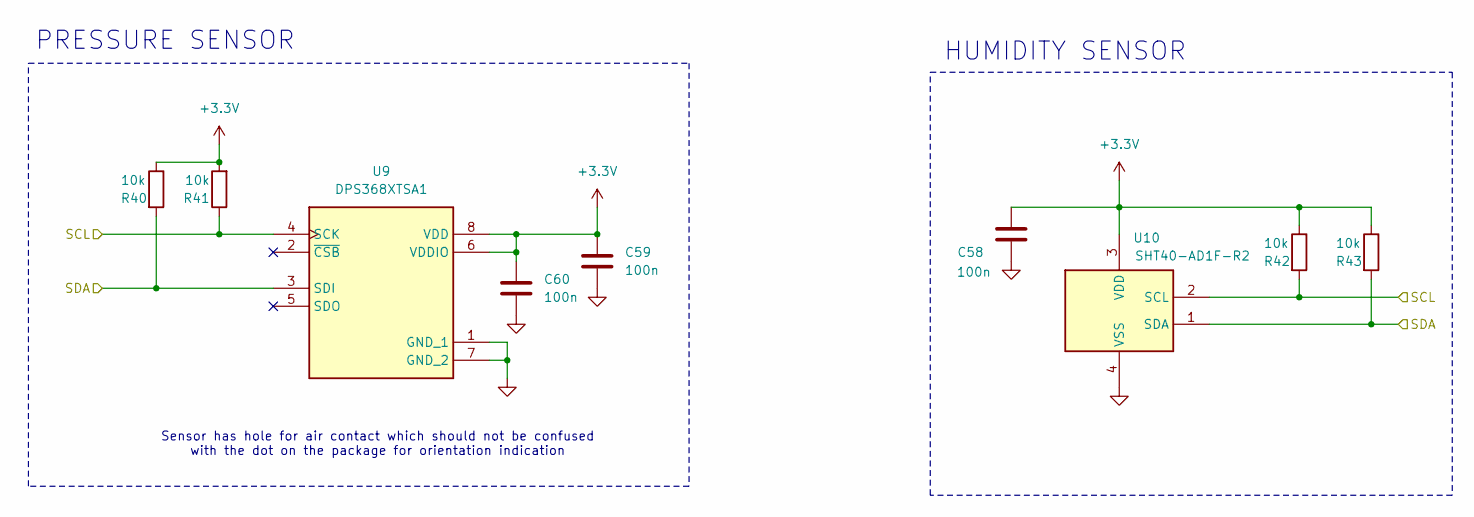
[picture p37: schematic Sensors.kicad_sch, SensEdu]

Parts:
C58, C59, C60: 100n; C_0603_1608Metric
R40, R41, R42, R43: 10k; R_0603_1608Metric
U9: DPS368XTSA1; Mouser Part Number 726-DPS368XTSA1
U10: SHT40-AD1F-R2; SHT40AD1FR2; Manufacturer_Part_Number SHT40-AD1F-R2; Mouser Part Number 403-SHT40-AD1F-R2

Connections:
+3.3V: C58.2, C59.1, C60.1, R40.1, R41.2, R42.1, R43.1, U9.6 (VDDIO), U9.8 (VDD), U10.3 (VDD); also elsewhere on the board
/SCL: R41.1, R42.2, U9.4 (SCK), U10.2 (SCL); also elsewhere on the board
/SDA: R40.2, R43.2, U9.3 (SDI), U10.1 (SDA); also elsewhere on the board
GND: C58.1, C59.2, C60.2, U9.1 (GND_1), U9.7 (GND_2), U10.4 (VSS); also elsewhere on the board

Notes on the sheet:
Sensor has hole for air contact which should not be confused with the dot on the package for orientation indication
PRESSURE SENSOR
HUMIDITY SENSOR

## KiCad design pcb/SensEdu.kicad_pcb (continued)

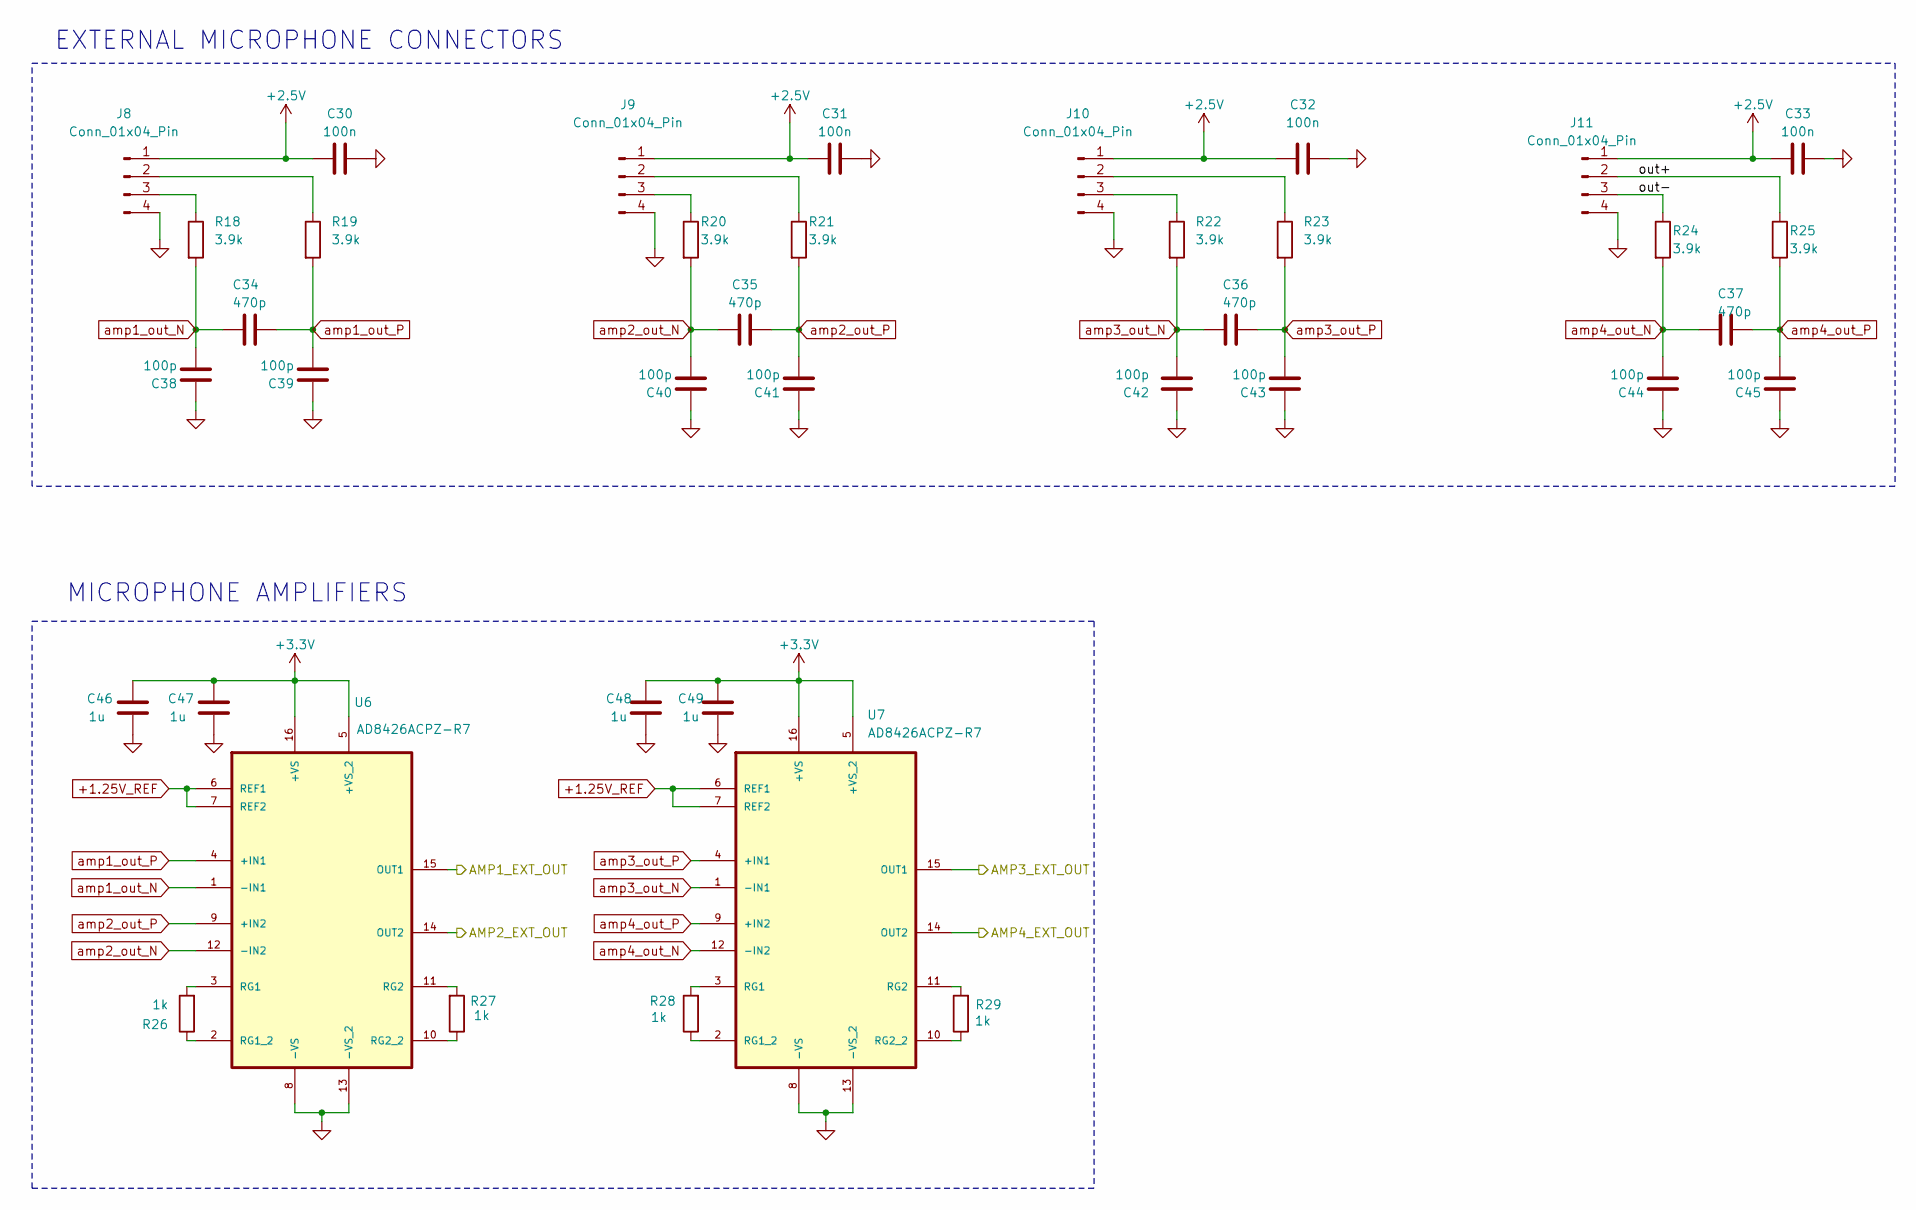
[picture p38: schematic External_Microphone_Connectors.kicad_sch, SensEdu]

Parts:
C30, C31, C32, C33: 100n; C_0603_1608Metric
C34, C35, C36, C37: 470p; C_0603_1608Metric
C38, C39, C40, C41, C42, C43, C44, C45: 100p; C_0603_1608Metric
C46, C47, C48, C49: 1u; C_0603_1608Metric
J8, J9, J10, J11: Conn_01x04_Pin; PinSocket_1x04_P2.54mm_Vertical
R18, R19, R20, R21, R22, R23, R24, R25: 3.9k; R_0603_1608Metric
R26, R27, R28, R29: 1k; R_0603_1608Metric
U6, U7: AD8426ACPZ-R7; QFN65P400X400X100-16N; MPN AD8426ACPZ-R7

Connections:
+1.25V_REF: U6.6 (REF1), U6.7 (REF2), U7.6 (REF1), U7.7 (REF2); also elsewhere on the board
+2.5V: C30.1, C31.1, C32.1, C33.1, J8.1, J9.1, J10.1, J11.1; also elsewhere on the board
+3.3V: C46.1, C47.1, C48.1, C49.1, U6.5 (+VS_2), U6.16 (+VS), U7.5 (+VS_2), U7.16 (+VS); also elsewhere on the board
/AMP1_OUT: U6.15 (OUT1); also elsewhere on the board
/AMP2_OUT: U6.14 (OUT2); also elsewhere on the board
/AMP3_OUT: U7.15 (OUT1); also elsewhere on the board
/AMP4_OUT: U7.14 (OUT2); also elsewhere on the board
/Microphones/External Microphone Connectors/out+: J11.2, R25.1
/Microphones/External Microphone Connectors/out-: J11.3, R24.1
GND: C30.2, C31.2, C32.2, C33.2, C38.1, C39.1, C40.1, C41.1, C42.1, C43.1, C44.1, C45.1, C46.2, C47.2, C48.2, C49.2, J8.4, J9.4, J10.4, J11.4, U6.8 (-VS), U6.13 (-VS_2), U7.8 (-VS), U7.13 (-VS_2); also elsewhere on the board
unnamed: J8.2, R19.1
unnamed: J8.3, R18.1
unnamed: J9.2, R21.1
unnamed: J9.3, R20.1
unnamed: J10.2, R23.1
unnamed: J10.3, R22.1
unnamed: R26.2, U6.3 (RG1)
unnamed: R26.1, U6.2 (RG1_2)
unnamed: R27.2, U6.11 (RG2)
unnamed: R27.1, U6.10 (RG2_2)
unnamed: R28.2, U7.3 (RG1)
unnamed: R28.1, U7.2 (RG1_2)
unnamed: R29.2, U7.11 (RG2)
unnamed: R29.1, U7.10 (RG2_2)
amp1_out_N: C34.2, C38.2, R18.2, U6.1 (-IN1)
amp1_out_P: C34.1, C39.2, R19.2, U6.4 (+IN1)
amp2_out_N: C35.2, C40.2, R20.2, U6.12 (-IN2)
amp2_out_P: C35.1, C41.2, R21.2, U6.9 (+IN2)
amp3_out_N: C36.2, C42.2, R22.2, U7.1 (-IN1)
amp3_out_P: C36.1, C43.2, R23.2, U7.4 (+IN1)
amp4_out_N: C37.2, C44.2, R24.2, U7.12 (-IN2)
amp4_out_P: C37.1, C45.2, R25.2, U7.9 (+IN2)

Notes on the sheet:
MICROPHONE AMPLIFIERS
EXTERNAL MICROPHONE CONNECTORS

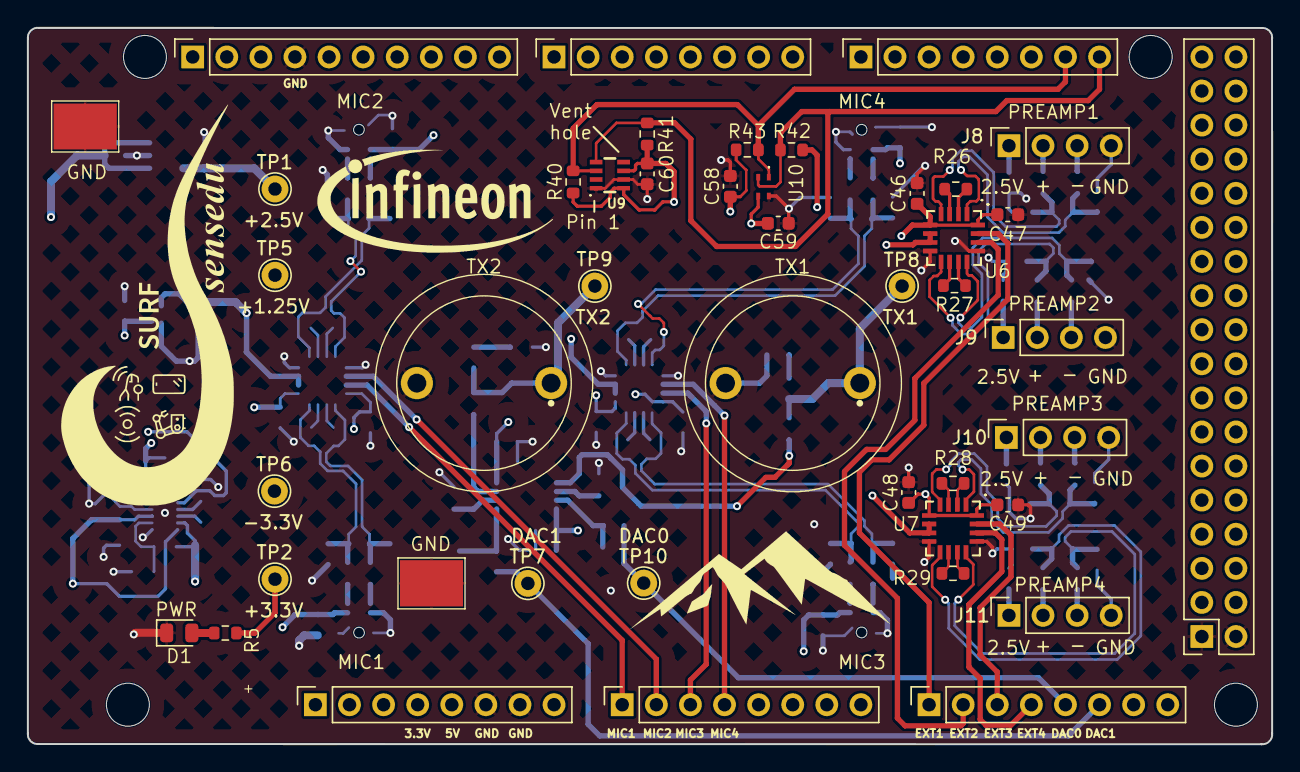
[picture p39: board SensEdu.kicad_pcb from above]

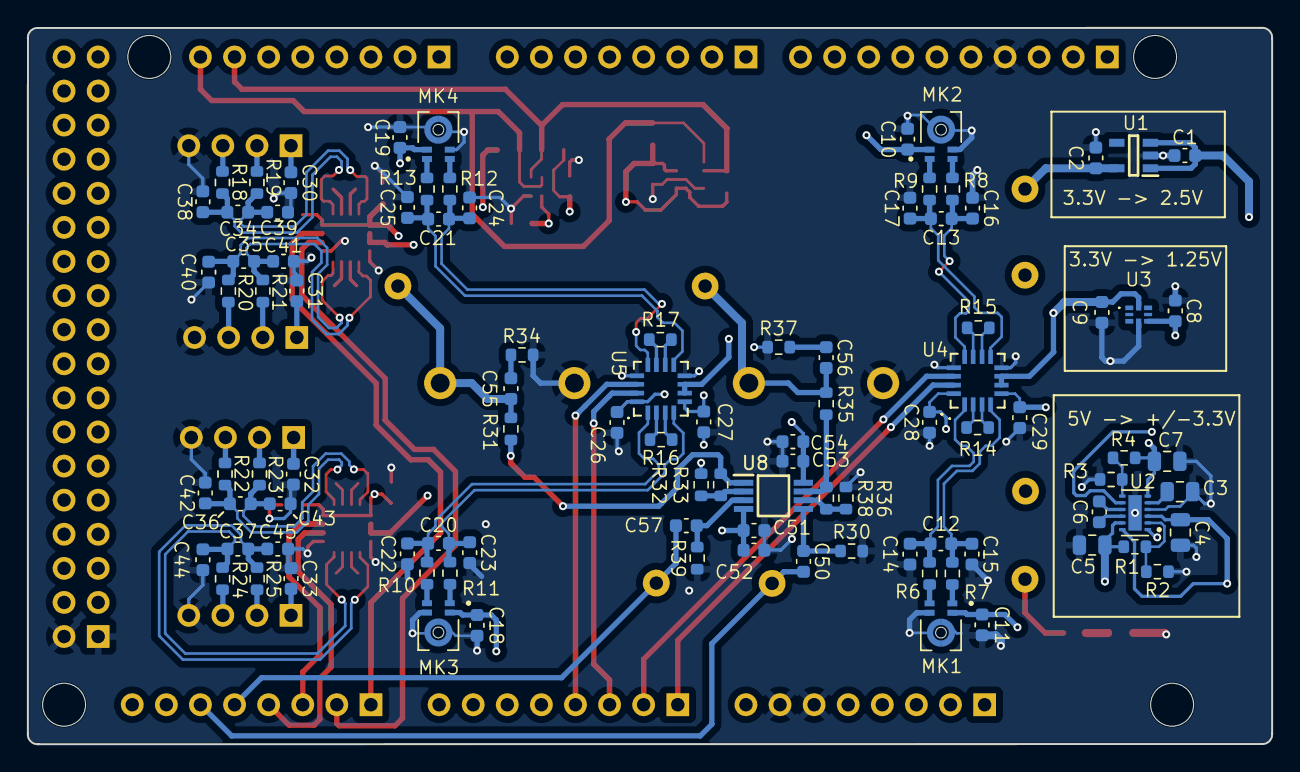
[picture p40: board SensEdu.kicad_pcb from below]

Board: 4 copper layers, 92.7 x 53.4 mm, 145 parts (97 on the bottom side), 83 nets.

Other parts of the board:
MH1, MH2, MH5, MH6: MountingHole_3.2mm

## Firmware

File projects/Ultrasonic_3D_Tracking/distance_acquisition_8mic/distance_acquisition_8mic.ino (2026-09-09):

/*
 * distance_acquisition_8mic
 *
 * Range acquisition front-end for 3D tracking. Emits a 32 kHz sine burst, then
 * records eight microphones across ADC1/ADC2/ADC3 and cross-correlates each
 * channel against the transmitted wave to find the echo delays.
 *
 * Only the resulting distances are sent to MATLAB, which trilaterates them into
 * a 3D position with an extended Kalman filter (matlab/online_ekf_8mic.m).
 *
 * The speaker couples directly into the microphones, so the first
 * BAN_DISTANCE cm worth of samples is blanked before peak search.
 *
 * A measurement is triggered by the character 't' on serial.
 */

#include "SensEdu.h"
#include "CMSIS_DSP.h"
#include "SineLUT.h"
#include "FilterTaps.h"
#include "DACWave.h"
#include "Peaks.h"

#include <vector>
#include <array>


uint32_t lib_error = 0;
uint8_t error_led = D86;

#define AIR_SPEED               343
#define AIR_SPEED_MM_S          (AIR_SPEED * 1000UL)
#define AIR_SPEED_UM_S          (AIR_SPEED * 1000000UL)
#define HALF_AIR_SPEED_MM_S     (AIR_SPEED_MM_S / 2U)
#define HALF_AIR_SPEED_UM_S     (AIR_SPEED_UM_S / 2U)

/* -------------------------------------------------------------------------- */
/*                                  Settings                                  */
/* -------------------------------------------------------------------------- */

#define BAN_DISTANCE	            25	        // Min distance [cm] - how many self reflections cancelled
#define SAMPLING_RATE               250000      // ADC sampling rate
#define STORE_BUF_SIZE              4096        // 2400 for 1 measurement per second 
                            	            

/* --------------------------------- Filter --------------------------------- */

#define FILTER_BLOCK_LENGTH     32      // Samples processed per call to the FIR process function

static float32_t fir_state_buffer[FILTER_BLOCK_LENGTH + FILTER_TAP_NUM - 1]; // Current filter state buffer
arm_fir_instance_f32 fir_filt;

/* ----------------------------------- ADC ---------------------------------- */

const uint16_t adc13_data_size = STORE_BUF_SIZE * 3;
const uint16_t adc2_data_size = STORE_BUF_SIZE * 2;

SENSEDU_ADC_BUFFER(mic123_data, adc13_data_size);
SENSEDU_ADC_BUFFER(mic48_data, adc2_data_size);
SENSEDU_ADC_BUFFER(mic567_data, adc13_data_size);


ADC_TypeDef* adc1 = ADC1;
ADC_TypeDef* adc2 = ADC2;
ADC_TypeDef* adc3 = ADC3;

const uint8_t adc1_mic_num = 3;
const uint8_t adc2_mic_num = 2;
const uint8_t adc3_mic_num = 3;

uint8_t mic123_pins[adc1_mic_num] = {A1, A3, A4};
uint8_t mic48_pins[adc2_mic_num] = {A5, A10};
uint8_t mic567_pins[adc3_mic_num] = {A6, A8, A9};


SensEdu_ADC_Settings adc1_settings = {
    .adc = adc1,
    .pins = mic123_pins,
    .pin_num = adc1_mic_num,

    .sr_mode = SENSEDU_ADC_SR_MODE_FIXED,
    .sampling_rate_hz = 250000,
    
    .adc_mode = SENSEDU_ADC_MODE_DMA_NORMAL,
    .mem_address = (uint16_t*)mic123_data,
    .mem_size = adc13_data_size
};

SensEdu_ADC_Settings adc2_settings = {
    .adc = adc2,
    .pins = mic48_pins,
    .pin_num = adc2_mic_num,

    .sr_mode = SENSEDU_ADC_SR_MODE_FIXED,
    .sampling_rate_hz = 250000,
    
    .adc_mode = SENSEDU_ADC_MODE_DMA_NORMAL,
    .mem_address = (uint16_t*)mic48_data,
    .mem_size = adc2_data_size
};

SensEdu_ADC_Settings adc3_settings = {
    .adc = adc3,
    .pins = mic567_pins,
    .pin_num = adc3_mic_num,

    .sr_mode = SENSEDU_ADC_SR_MODE_FIXED,
    .sampling_rate_hz = 250000,
    
    .adc_mode = SENSEDU_ADC_MODE_DMA_NORMAL,
    .mem_address = (uint16_t*)mic567_data,
    .mem_size = adc13_data_size
};

/* ----------------------------------- DAC ---------------------------------- */

#define DAC_SINE_FREQ     	32000                           // 32kHz
#define DAC_SAMPLE_RATE     DAC_SINE_FREQ * sine_lut_size   // 64 samples per one sine cycle

DAC_Channel* dac_channel = DAC_CH1;
SensEdu_DAC_Settings dac_settings = {
    .dac_channel = dac_channel, 
    .sampling_freq = DAC_SAMPLE_RATE,
    .mem_address = (uint16_t*)sine_lut,
    .mem_size = sine_lut_size,
    .wave_mode = SENSEDU_DAC_MODE_BURST_WAVE,
    .burst_num = dac_cycle_num
};

/* -------------------------------------------------------------------------- */
/*                                  Constants                                 */
/* -------------------------------------------------------------------------- */

const uint16_t air_speed = AIR_SPEED; // m/s

// e.g. 25cm ban means 0.25*2/343 time ban, then multiply by sample rate
const uint32_t c_banned_sample_num = ((BAN_DISTANCE*2*SAMPLING_RATE)/air_speed)/100; 


/* -------------------------------------------------------------------------- */
/*                              Global Structure                              */
/* -------------------------------------------------------------------------- */

typedef struct {
	uint8_t ban_flag; // Activate self reflections ban
	char serial_read_buf;
    float processing_buffer[STORE_BUF_SIZE]; // Reusable float buffer for signal processing
    uint16_t channel_buffer[STORE_BUF_SIZE]; // Data rearrangement
} SenseduBoard;

static SenseduBoard sensedu_board;

/* -------------------------------------------------------------------------- */
/*                                    Setup                                   */
/* -------------------------------------------------------------------------- */

void setup() {
	SenseduBoard* main_obj_ptr = &sensedu_board;
	main_obj_init(main_obj_ptr);

    // Initializing the filter
    arm_fir_init_f32(&fir_filt, FILTER_TAP_NUM, filter_taps, fir_state_buffer, FILTER_BLOCK_LENGTH); 

    Serial.begin(115200);

    // DAC
    SensEdu_DAC_Init(&dac_settings);
    
    // ADC1
    SensEdu_ADC_Init(&adc1_settings);
    SensEdu_ADC_Enable(adc1);

    // ADC2
    SensEdu_ADC_Init(&adc2_settings);
    SensEdu_ADC_Enable(adc2);

    // ADC3
    SensEdu_ADC_Init(&adc3_settings);
    SensEdu_ADC_Enable(adc3);
    
    pinMode(error_led, OUTPUT);
    digitalWrite(error_led, HIGH);
    check_lib_errors();
}

/* -------------------------------------------------------------------------- */
/*                                    Loop                                    */
/* -------------------------------------------------------------------------- */

void loop() {
	SenseduBoard* main_obj_ptr = &sensedu_board;
    // Wait for the trigger character 't' from the host
    char c;
    while (true) {
        if (Serial.available() > 0) {
            c = Serial.read();
            if (c == 't') {
                break;
            }
        }
        delay(1);
    }
    
    // Start the DAC -> ADC sequence
    SensEdu_DAC_Enable(dac_channel);
    while (!SensEdu_DAC_GetBurstCompleteFlag(dac_channel)); // Wait for dac to finish sending the burst
    SensEdu_DAC_ClearBurstCompleteFlag(dac_channel); 
    
    // Start ADCs
    SensEdu_ADC_Start(adc1);
    SensEdu_ADC_Start(adc2);
    SensEdu_ADC_Start(adc3);

    while (!SensEdu_ADC_IsDmaTransferComplete(adc1));
    SensEdu_ADC_ClearDmaTransferComplete(adc1);

    while (!SensEdu_ADC_IsDmaTransferComplete(adc2));
    SensEdu_ADC_ClearDmaTransferComplete(adc2);

    while (!SensEdu_ADC_IsDmaTransferComplete(adc3));
    SensEdu_ADC_ClearDmaTransferComplete(adc3);

    // Calculating distances for each microphone
    uint32_t peaks[MAX_PEAKS]; // Strongest MAX_PEAKS reflections per channel
    static std::vector<uint32_t> distances;
    distances.reserve((adc1_mic_num + adc2_mic_num + adc3_mic_num)*MAX_PEAKS);

    for (uint8_t i = 0; i < adc1_mic_num; i++) {
        get_channel_data(mic123_data, main_obj_ptr->channel_buffer, STORE_BUF_SIZE, adc1_mic_num, i);
        process_data(main_obj_ptr->processing_buffer, STORE_BUF_SIZE, main_obj_ptr->channel_buffer, STORE_BUF_SIZE, main_obj_ptr->ban_flag);
        calculate_distances(main_obj_ptr->processing_buffer, STORE_BUF_SIZE, SAMPLING_RATE, peaks);
        for (uint8_t k = 0; k < MAX_PEAKS; k++) {
            distances.push_back(peaks[k]);
        }
    }
    for (uint8_t i = 0; i < adc2_mic_num; i++) {
        get_channel_data(mic48_data, main_obj_ptr->channel_buffer, STORE_BUF_SIZE, adc2_mic_num, i);
        process_data(main_obj_ptr->processing_buffer, STORE_BUF_SIZE, main_obj_ptr->channel_buffer, STORE_BUF_SIZE, main_obj_ptr->ban_flag);
        calculate_distances(main_obj_ptr->processing_buffer, STORE_BUF_SIZE, SAMPLING_RATE, peaks);
        for (uint8_t k = 0; k < MAX_PEAKS; k++) {
            distances.push_back(peaks[k]);
        }
    }
    for (uint8_t i = 0; i < adc3_mic_num; i++) {
        get_channel_data(mic567_data, main_obj_ptr->channel_buffer, STORE_BUF_SIZE, adc3_mic_num, i);
        process_data(main_obj_ptr->processing_buffer, STORE_BUF_SIZE, main_obj_ptr->channel_buffer, STORE_BUF_SIZE, main_obj_ptr->ban_flag);
        calculate_distances(main_obj_ptr->processing_buffer, STORE_BUF_SIZE, SAMPLING_RATE, peaks);
        for (uint8_t k = 0; k < MAX_PEAKS; k++) {
            distances.push_back(peaks[k]);
        }
    }

    // Sending the distance measurements
    for (uint8_t i = 0; i < (adc1_mic_num + adc2_mic_num + adc3_mic_num)*MAX_PEAKS; i++) {
        Serial.write((const uint8_t *) &distances[i], 4);
    }

    check_lib_errors();
    distances.clear();
}

void process_data(float* buf, const uint16_t buf_size, uint16_t* ch_array, const uint16_t ch_array_size, uint8_t ban_flag) {

    /* --------------------- RESCALED, FILTERED, NO COUPLED --------------------- */
    // Rescale from [0, (2^16-1)] to [-1, 1] and filter around 32 kHz
    clear_float_buf(buf, buf_size);
    rescale_adc_wave(buf, ch_array, ch_array_size);
    filter_32kHz_wave(buf, buf_size);
    if (ban_flag == 1) {
        remove_coupling(buf, c_banned_sample_num);
    } 
    /* ---------------------------------- XCORR --------------------------------- */
	custom_xcorr(buf, dac_wave, buf_size);
    
}

void transfer_serial_data(uint16_t* data, const uint16_t data_length, const uint16_t chunk_size_byte) {
    for (uint16_t i = 0; i < (data_length*2); i += chunk_size_byte) {
        uint16_t transfer_size = ((data_length*2) - i < chunk_size_byte) ? (data_length*2 - i) : chunk_size_byte;
        Serial.write((const uint8_t *) data + i, transfer_size);
    }
}

void transfer_serial_data_float(float* data, const uint16_t data_length, const uint16_t chunk_size_byte) {
    for (uint16_t i = 0; i < (data_length*4); i += chunk_size_byte) {
        uint16_t transfer_size = ((data_length*4) - i < chunk_size_byte) ? (data_length*4 - i) : chunk_size_byte;
        Serial.write((const uint8_t *) data + i, transfer_size);
    }
}

void check_lib_errors() {
    lib_error = SensEdu_GetError();
    while (lib_error != 0) {
        digitalWrite(error_led, LOW);
    }
}

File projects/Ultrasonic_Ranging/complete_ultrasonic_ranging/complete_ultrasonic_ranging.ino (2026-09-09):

/*
 * complete_ultrasonic_ranging
 *
 * Pulse-echo ultrasonic ranging. Emits a 32 kHz sine burst on the speaker,
 * records four microphones at 250 kS/s, and cross-correlates each channel
 * against the transmitted wave to find the echo delay.
 *
 * All signal processing runs on the board, so only the resulting distances are
 * sent to MATLAB. Set IS_TRANSMIT_DETAILED_DATA to also stream the raw,
 * filtered and cross-correlated waveforms for debugging.
 *
 * The speaker couples directly into the microphones, so the first
 * BAN_DISTANCE cm worth of samples is blanked before peak search.
 *
 * A measurement is triggered by the character 't' on serial.
 */

#include "SensEdu.h"
#include "CMSIS_DSP.h"
#include "SineLUT.h"
#include "FilterTaps.h"
#include "DACWave.h" // Contains wave and its size
#include "Peaks.h"

#include <math.h>
#include <vector>
#include <array>

uint32_t lib_error = 0;
uint8_t error_led = D86;

#define AIR_SPEED               343
#define AIR_SPEED_MM_S          (AIR_SPEED * 1000UL)
#define AIR_SPEED_UM_S          (AIR_SPEED * 1000000UL)
#define HALF_AIR_SPEED_MM_S     (AIR_SPEED_MM_S / 2U)
#define HALF_AIR_SPEED_UM_S     (AIR_SPEED_UM_S / 2U)

/* -------------------------------------------------------------------------- */
/*                                  Settings                                  */
/* -------------------------------------------------------------------------- */

#define IS_TRANSMIT_DETAILED_DATA   false    // Activate full raw, filtered, xcorr data transmission
#define BAN_DISTANCE	            20	    // Min distance [cm] - how many self reflections cancelled
#define SAMPLING_RATE               250000  // You need to measure this value using a wave generator with a fixed e.g. 1kHz Sine
#define STORE_BUF_SIZE              2048    // 2400 for 1 measurement per second. 

/* --------------------------------- Filter --------------------------------- */
#define FILTER_BLOCK_LENGTH     32      // Samples processed per call to the FIR process function

static float32_t fir_state_buffer[FILTER_BLOCK_LENGTH + FILTER_TAP_NUM - 1]; // Current filter state buffer
arm_fir_instance_f32 fir_filt;

/* ----------------------------------- ADC ---------------------------------- */
const uint16_t mic_data_size = STORE_BUF_SIZE * 2;
SENSEDU_ADC_BUFFER(mic12_data, mic_data_size);
SENSEDU_ADC_BUFFER(mic34_data, mic_data_size);

// Standard 4-microphone SensEdu board
ADC_TypeDef* adc1 = ADC1;
ADC_TypeDef* adc2 = ADC2;
const uint8_t adc1_mic_num = 2;
const uint8_t adc2_mic_num = 2;
uint8_t mic12_pins[adc1_mic_num] = {A0, A1};
uint8_t mic34_pins[adc2_mic_num] = {A2, A3};

SensEdu_ADC_Settings adc1_settings = {
    .adc = adc1,
    .pins = mic12_pins,
    .pin_num = adc1_mic_num,

    .sr_mode = SENSEDU_ADC_SR_MODE_FIXED,
    .sampling_rate_hz = 250000,
    
    .adc_mode = SENSEDU_ADC_MODE_DMA_NORMAL,
    .mem_address = (uint16_t*)mic12_data,
    .mem_size = mic_data_size
};

SensEdu_ADC_Settings adc2_settings = {
    .adc = adc2,
    .pins = mic34_pins,
    .pin_num = adc2_mic_num,

    .sr_mode = SENSEDU_ADC_SR_MODE_FIXED,
    .sampling_rate_hz = 250000,
    
    .adc_mode = SENSEDU_ADC_MODE_DMA_NORMAL,
    .mem_address = (uint16_t*)mic34_data,
    .mem_size = mic_data_size
};

/* ----------------------------------- DAC ---------------------------------- */

#define DAC_SINE_FREQ     	32000                           // 32kHz
#define DAC_SAMPLE_RATE     DAC_SINE_FREQ * sine_lut_size   // 64 samples per one sine cycle

DAC_Channel* dac_channel = DAC_CH2;
SensEdu_DAC_Settings dac_settings = {
    .dac_channel = dac_channel, 
    .sampling_freq = DAC_SAMPLE_RATE,
    .mem_address = (uint16_t*)sine_lut,
    .mem_size = sine_lut_size,
    .wave_mode = SENSEDU_DAC_MODE_BURST_WAVE,
    .burst_num = dac_cycle_num
};

/* -------------------------------------------------------------------------- */
/*                                  Constants                                 */
/* -------------------------------------------------------------------------- */

const uint16_t air_speed = AIR_SPEED; // m/s

// e.g. 25cm ban means 0.25*2/343 time ban, then multiply by sample rate
const uint32_t c_banned_sample_num = ((BAN_DISTANCE*2*SAMPLING_RATE)/air_speed)/100;
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

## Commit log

2025-10-01 sampled ref wave for xcorr script
2025-10-27 ADC2 sample rate in matlab same as arduino sketch
2025-11-10 docs: add improved pcb pictures
    add roadmap picture
    add 3d model for the speaker
    [Ultrasound shield.kicad_pcb]
2025-11-14 refactor: rename projects to lower case
2025-11-14 refactor: rename docs back to force lower case
2026-03-13 feat: EMG first stage processing
2026-03-31 refactor: rearrange folder structure
    [ground_t_1.csv, ground_t_2.csv, ground_t_3.csv, ground_t_4.csv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]
2026-04-28 refactor: Remove old PCB & SHT lib copy files
    [SHT35-DIS-B2.5KS.STEP, SHT35_Board-B_Cu.gbr, SHT35_Board-B_Mask.gbr, SHT35_Board-B_Paste.gbr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]
2026-04-29 feat: Add pressure trend linear regression
    - Refactor weather station styling
    - Split main sketch into modules
2026-05-08 feat: Improve pressure conversion formula
2026-05-15 feat: Add examples for temp/RH/pressure readings
2026-05-18 refactor: Rework Record_Audio for SDRAM buffering
    Firmware:
    - Capture into a ping-pong of SDRAM slots (SEGMENT_SECONDS each) and stream
    whole slots over USB instead of every DMA half-buffer
    - Framed protocol: 20-byte segment headers and 16-byte command ACKs, both
    carrying a session_id so the host can detect stale/cross-session bytes
    - Commands 's', 'p', and '?' (status); 's' is idempotent and forces a clean
    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
2026-05-18 refactor: Tighten Record_Audio cmd_start ordering
    - cmd_start emits the ACK before SensEdu_ADC_Start
    - process_usb_transfer picks the ready slot with the lowest sequence_id
    - MATLAB seg_is_valid now takes expected_session_id and the actual
    SEGMENT_SAMPLES
2026-05-18 refactor: Use bytes instead of samples in MATLAB
2026-05-20 refactor: Final arduino sketch rearrangement
2026-06-05 Revert "temp"
    This reverts commit 1524a160d4631e6d67c67fc9e2f5361331d022c1.
    [EMG-BioInputs-BOM.xlsx]
2026-06-08 feat: Add `_C` pin shorts for ADC flexibility
    - Update setup pictures to SensEdu 0.8 PCB
2026-06-08 refactor: Cleanup arduino sketch
2026-06-08 refactor: Rename EMG PCB adapter to Header
    [EMG-BioInputs-BOM.xlsx, MiniJack2Header-BOM.csv, MiniJack2Header-B_Cu.gbr, MiniJack2Header-B_Mask.gbr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]
2026-06-17 fix: Change header pin layout for SensEdu 0.8+
    [MiniJack2Header-BOM.csv, MiniJack2Header-B_Cu.gbr, MiniJack2Header-B_Mask.gbr, MiniJack2Header-B_Paste.gbr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]
